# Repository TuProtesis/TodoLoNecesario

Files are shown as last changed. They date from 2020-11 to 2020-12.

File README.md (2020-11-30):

# TodoLoNecesario
Este repositorio contiene todos los archivos necesarios para guiarte en el proceso de ensamblado de tu prótesis.
Primero, compre todos los materiales de la lista de compra.
Luego, descarge todos los documentos del repositorio.
Por último, siga paso a paso las instrucciones del archivo "Manual para ensamblado de la prótesis".

Nota: Debe descargar el pdf "Lista de materiales de la protesis" para poder acceder a los enlaces de compra proporcionados.

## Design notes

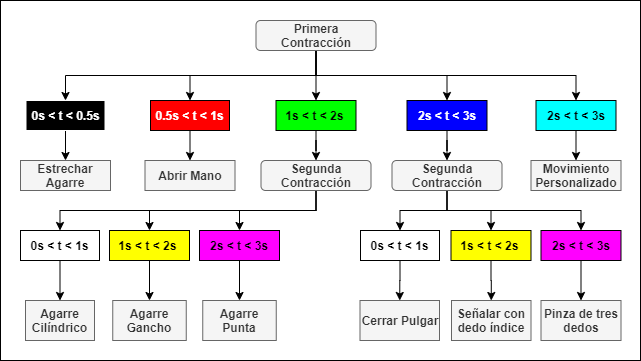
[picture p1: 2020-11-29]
Secuencias de Uso.png

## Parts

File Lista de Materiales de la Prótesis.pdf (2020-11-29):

# Lista de Materiales de la Prótesis

Materiales | Imagen del elemento | Precio unidad (USD) | Precio total (USD) | Lugar para comprar | Disponibilidad en Rep. Dom.
1x HATCHBOX PLA 3D Printer Filament, 1 kg Spool, 1.75 mm | | $19.99 | $19.99 | Amazon (https://www.amazon.com/-/es/filamento-impresora-3D-precisi%C3%B3n-dimensional/dp/B015I1CYFE?__mk_es_US=%C3%85M%C3%85%C5%BD%C3%95%C3%91) | En pocos lugares, recomendable comprar en el enlace proporcionado por nosotros.
1x Seamuing 6Pcs MG90S Micro Servo 9G | | $20.99 | $20.99 | Amazon (https://www.amazon.com/-/es/engranado-Helic%C3%B3ptero-Compatible-Raspberry-Proyecto/dp/B08BJPNTX9?__mk_es_US=%C3%85M%C3%85%C5%BD%C3%95%C3%91) | En pocos lugares, recomendable comprar en el enlace proporcionado por nosotros.
1x Minicargador portátil de 10000 mAh | | $16.99 | $16.99 | Amazon (https://www.amazon.com/-/es/Cargador-tel%C3%A9fono-port%C3%A1til-Powerpack-Compatible/dp/B07VGHLRTQ?__mk_es_US=%C3%85M%C3%85%C5%BD%C3%95%C3%91) | En pocos lugares, recomendable comprar en el enlace proporcionado por nosotros.
1x Hosyond Nano V3.0 ATmega328P | | $4.33 | $4.33 | Amazon (https://www.amazon.com/-/es/gp/product/B08915GQ89/ref=ppx_yo_dt_b_asin_title_o01_s00?ie=UTF8&psc=1) | En pocos lugares, recomendable comprar en el enlace proporcionado por nosotros.
1x Interruptor Pulsador | | $0.3 | $0.3 | Cabletronica | Puede comprarse en tiendas de internet si se desea. Enlace de Amazon. (https://www.amazon.com/dp/B00R17XUFC/ref=cm_sw_r_wa_apa_fabt1_ZG.WFb8VY8CMB)
1x Correa Velcro | | $3.07 | $6.15 | Ferretería Cuesta | Preferiblemente comprar en tiendas en el país.
1x Ácido muriático (Ácido Clorhídrico) | | $2.56 | $2.56 | Almacenes unidos | Preferiblemente comprar en tiendas en el país.
1x Agua oxigenada 30% | | $0.68 | $0.68 | Almacenes unidos | Preferiblemente comprar en tiendas en el país.

1x Acetona | $0.51 | $0.51 | Farmacia Farma Value | Preferiblemente comprar en tiendas en el país .
1x Baquelita ónica electr | $1 | $1 | Cabletronica | Puede comprarse en tiendas de internet si se desea . Enlace de Amazon . (https://www.amazon.com/-/es/laminado-unidades-laminada-bricolaje-circuito/dp/B01MCVLDDZ)
Resistencias 2 de 100 ohms 2 de 1k ohms 1 de 2k ohms 1 de 220 ohm s Total: 6 | $0.017 | $0.10 | Cabletrónica | Puede comprarse en tiendas de internet si se desea . Enlace de Amazon . (https://www.amazon.com/-/es/valores-resistencias-resistencia-proyectos-experimentos/dp/B07BKRS4QZ)
1x Led RGB | $0.09 | $0.09 | Cabletronica | Puede comprarse en tiendas de internet si se desea . Enlace de Amazon . (https://www.amazon.com/-/es/Tri-Color-Multicolor-Resistencias-Incluido-emisores/dp/B077XGF3YR?__mk_es_US=%C3%85M%C3%85%C5%BD%C3%95%C3%91)
1x Pin header hembra | $1.79 | $1.79 | Cabletronica | Puede comprarse en tiendas de internet si se desea . Enlace de Amazon . (https://www.amazon.com/-/es/honbay-40-pines-hembra-conector-Arduino/dp/B06Y4S6G29?__mk_es_US=%C3%85M%C3%85%C5%BD%C3%95%C3%91&s=electronics)
Conector de crimpado (19 c/u. ) Total: 38 | $0.034 | $1.3 | Cabletr ónica | Puede comprarse en tiendas de internet si se desea .
1x Estaño para soldar | $3 | $3 | Cabletronica | Puede comprarse en tiendas de internet si se desea . Enlace de Amazon . (https://www.amazon.com/-/es/AUSTOR-60-40-soldadura-3-53-0-039/dp/B073LT2PKB?__mk_es_US=%C3%85M%C3%85%C5%BD%C3%95%C3%91)
1x Módulo Bluetooth 4.0 para Arduino iOS Android CC2540 CC2541 (2 unidades) | $4 | $4 | Amazon (https://www.amazon.com/-/es/gp/product/B01G9KSAF6/ref=ppx_yo_dt_b_asin_title_o07_s00?ie=UTF8&psc=1) | En pocos lugares, recomendable comprar en el enlace proporcionado por nosotros.

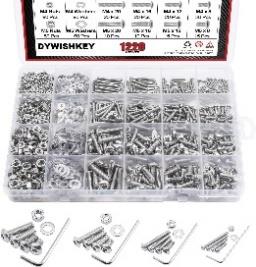
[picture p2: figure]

1x DYWISHKEY 1220 piezas M2 M3 M4 M5, 304 acero inoxidable hexagonal botón cabeza tornillos tuercas arandelas surtido Kit con llaves hexagonales | $26.98 | $26.98 | Amazon (https://www.amazon.com/-/es/DYWISHKEY-inoxidable-hexagonal-tornillos-hexagonales/dp/B07QLRKYR7?__mk_es_US=%C3%85M%C3%85%C5%BD%C3%95%C3%91) | Recomendable comprar los tornillos por separado en ferreterías del país . Pueden tener el tipo de cabeza que usted prefiera.

$
126.8

6 (USD)

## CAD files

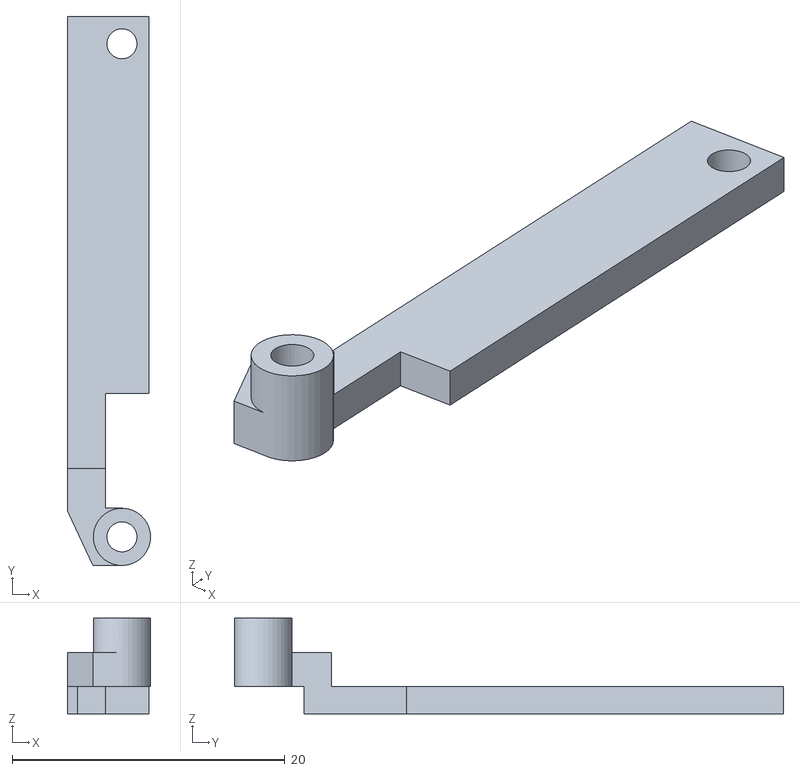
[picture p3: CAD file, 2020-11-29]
Impresión/Anular/Anular_Pieza5.STL
6.10 x 40.2 x 7.00

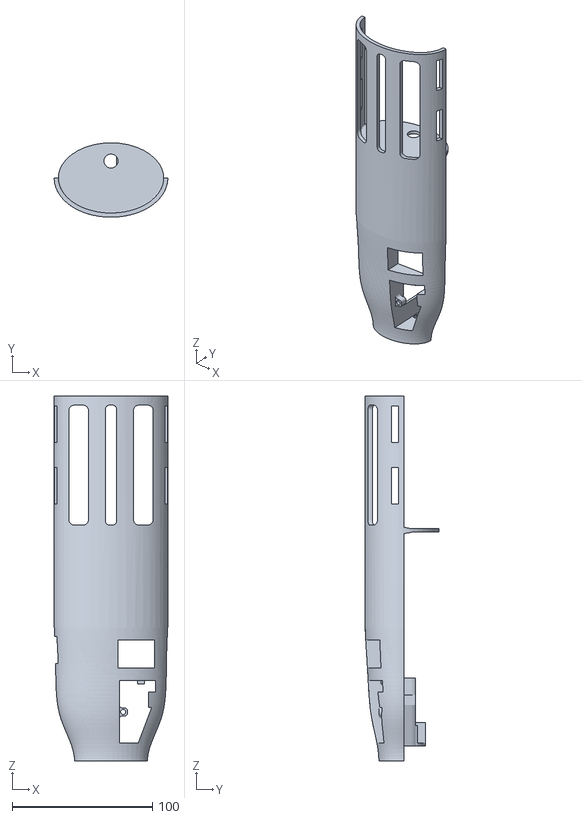
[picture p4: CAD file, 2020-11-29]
Impresión/Brazo/Brazo_Pieza15.STL
81.0 x 53.0 x 259.9

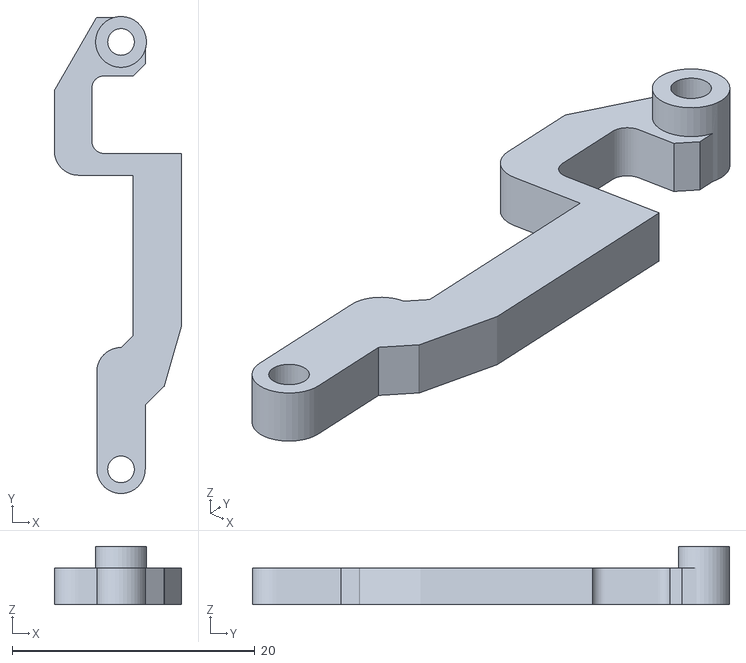
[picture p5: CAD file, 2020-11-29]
Impresión/Mayor/Mayor_Pieza6.STL
10.5 x 39.3 x 4.80

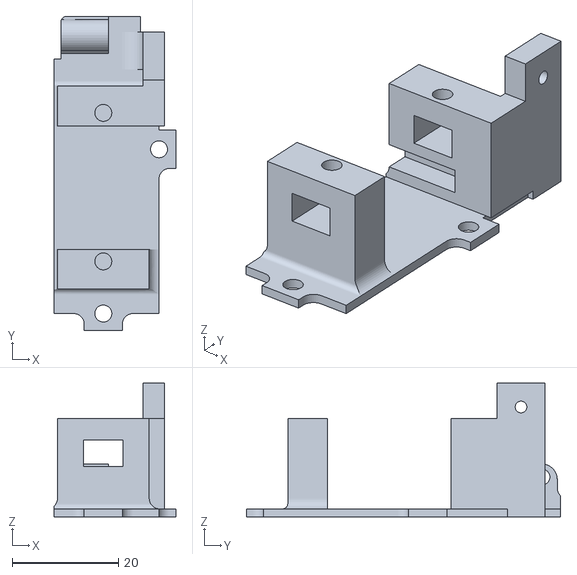
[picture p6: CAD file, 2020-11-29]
Impresión/Meñique/Meñique_Pieza1.STL
23.0 x 59.2 x 25.2

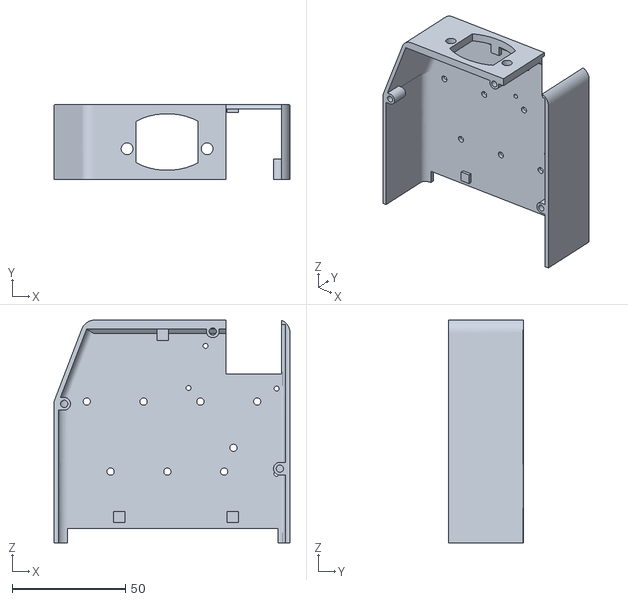
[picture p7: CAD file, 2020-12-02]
Impresión/Palma/Palma_Pieza12_para mano derecha.STL
104.3 x 33.0 x 98.5

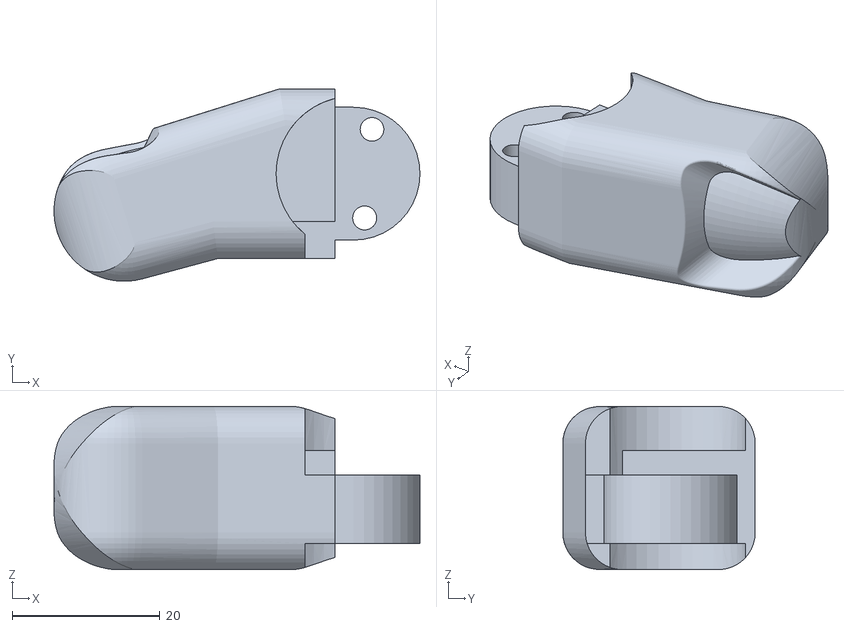
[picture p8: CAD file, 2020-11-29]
Impresión/Pulgar/Pulgar_Pieza7.STL
49.6 x 26.1 x 22.1

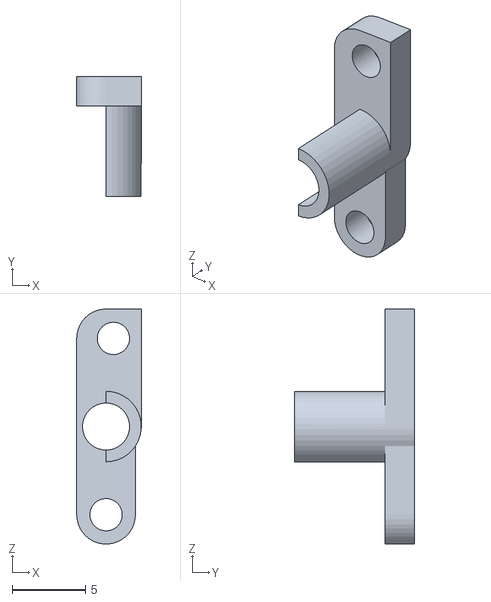
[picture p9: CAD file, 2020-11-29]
Impresión/Índice/Índice_Pieza4.STL
4.40 x 8.15 x 16.0

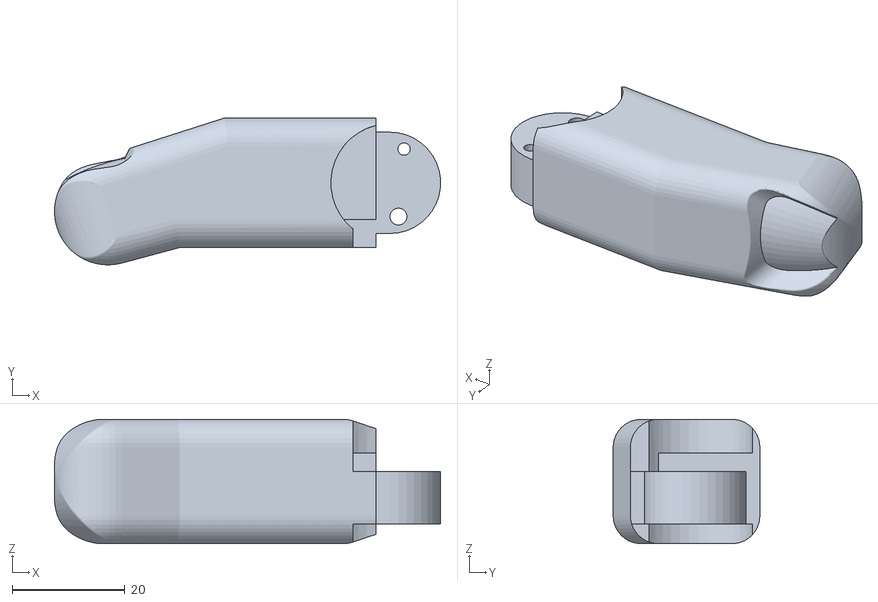
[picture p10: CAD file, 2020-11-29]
Impresión/Anular/Anular_Pieza7.STL
68.6 x 26.1 x 22.1

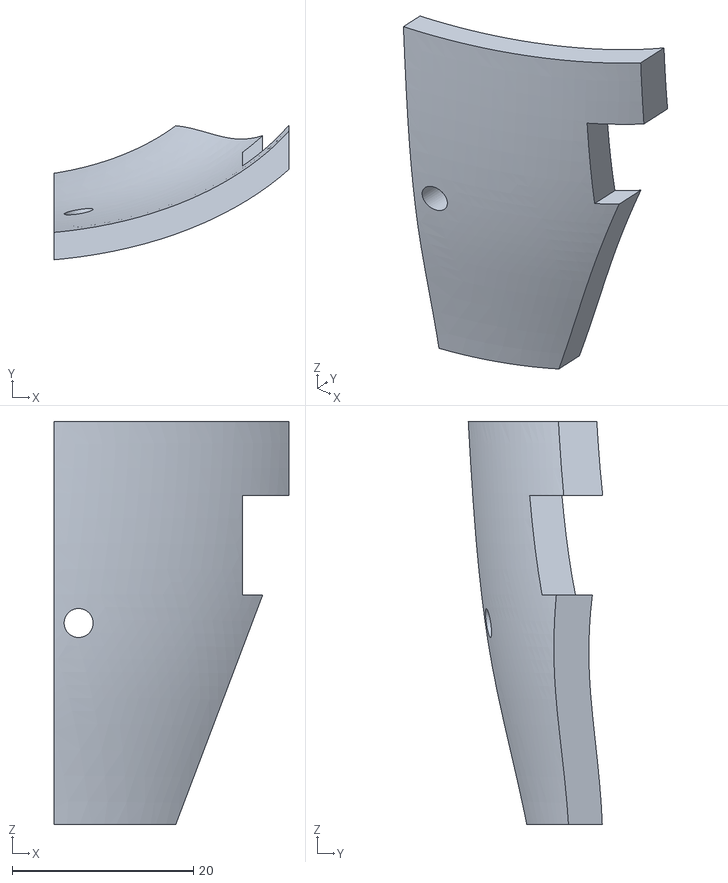
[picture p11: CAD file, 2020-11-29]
Impresión/Brazo/Brazo_Pieza17.STL
25.9 x 14.8 x 44.4

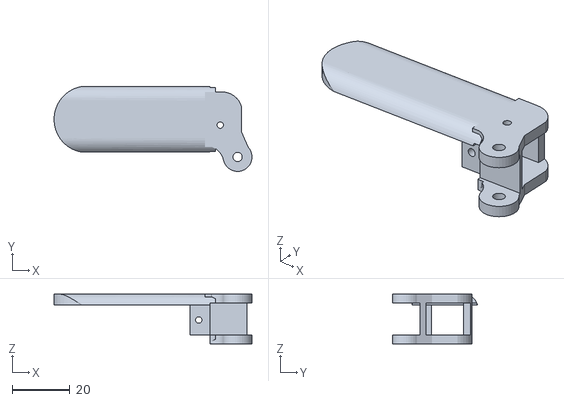
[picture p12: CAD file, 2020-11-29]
Impresión/Mayor/Mayor_Pieza9.STL
68.4 x 29.3 x 17.2

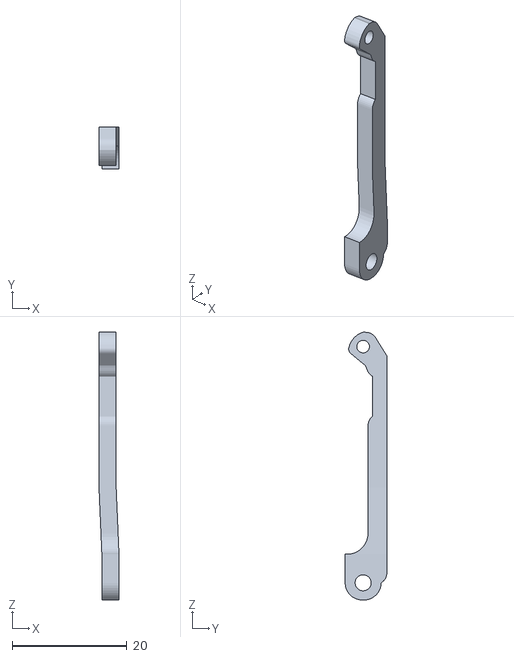
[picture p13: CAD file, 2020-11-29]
Impresión/Meñique/Meñique_Pieza3.STL
3.50 x 7.30 x 46.8

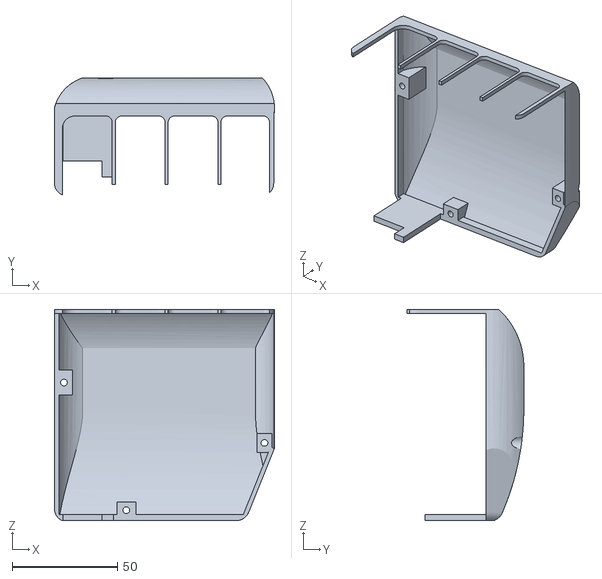
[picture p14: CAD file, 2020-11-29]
Impresión/Palma/Palma_Pieza14.STL
104.6 x 55.5 x 100.5

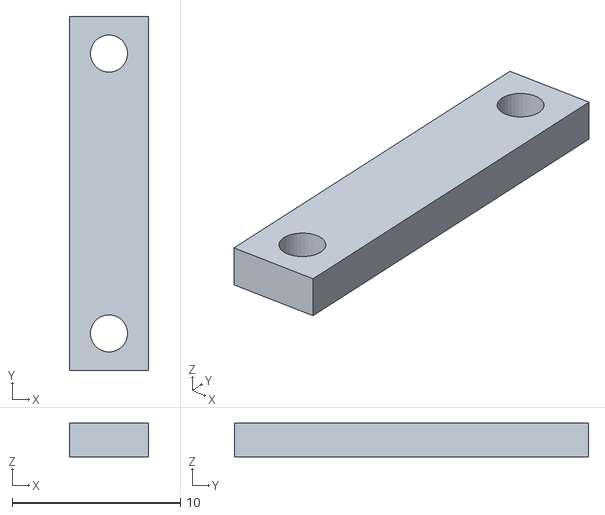
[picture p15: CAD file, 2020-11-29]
Impresión/Pulgar/Pulgar_Pieza10.STL
4.70 x 21.0 x 2.00

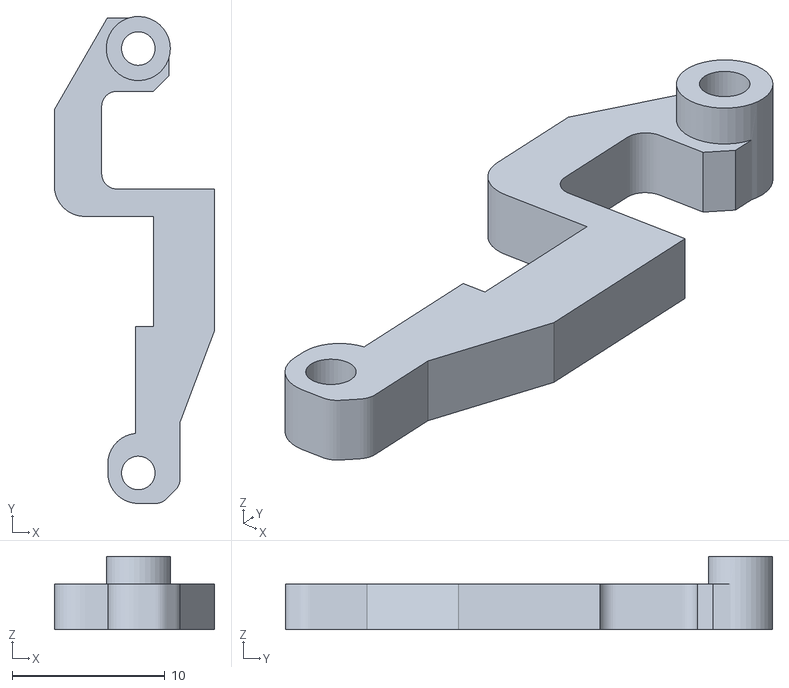
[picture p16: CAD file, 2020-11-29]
Impresión/Índice/Índice_Pieza6.STL
10.5 x 31.9 x 4.80

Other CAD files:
Impresión/Brazo/Brazo_Pieza16.STL
Impresión/Meñique/Meñique_Pieza8.STL
Impresión/Anular/Anular_Pieza2.STL
Impresión/Anular/Anular_Pieza4.STL
Impresión/Anular/Anular_Pieza6.STL
Impresión/Anular/Anular_Pieza8.STL
Impresión/Anular/Anular_Pieza9.STL
Impresión/Mayor/Mayor_Pieza2.STL
Impresión/Mayor/Mayor_Pieza4.STL
Impresión/Mayor/Mayor_Pieza5.STL
Impresión/Mayor/Mayor_Pieza8.STL
Impresión/Mayor/Mayor_pieza7.STL
Impresión/Meñique/Meñique_Pieza2.STL
Impresión/Meñique/Meñique_Pieza4.STL
Impresión/Meñique/Meñique_Pieza5.STL
Impresión/Meñique/Meñique_Pieza6.STL
Impresión/Meñique/Meñique_Pieza7.STL
Impresión/Meñique/Meñique_Pieza9.STL
Impresión/Palma/Palma_Pieza12_Para mano izquierda.STL
Impresión/Palma/Palma_Pieza13.STL
Impresión/Pulgar/Pulgar_Pieza11.STL
Impresión/Pulgar/Pulgar_Pieza8.STL
Impresión/Pulgar/Pulgar_Pieza9.STL
Impresión/Índice/Índice_Pieza1.STL
Impresión/Índice/Índice_Pieza2.STL
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

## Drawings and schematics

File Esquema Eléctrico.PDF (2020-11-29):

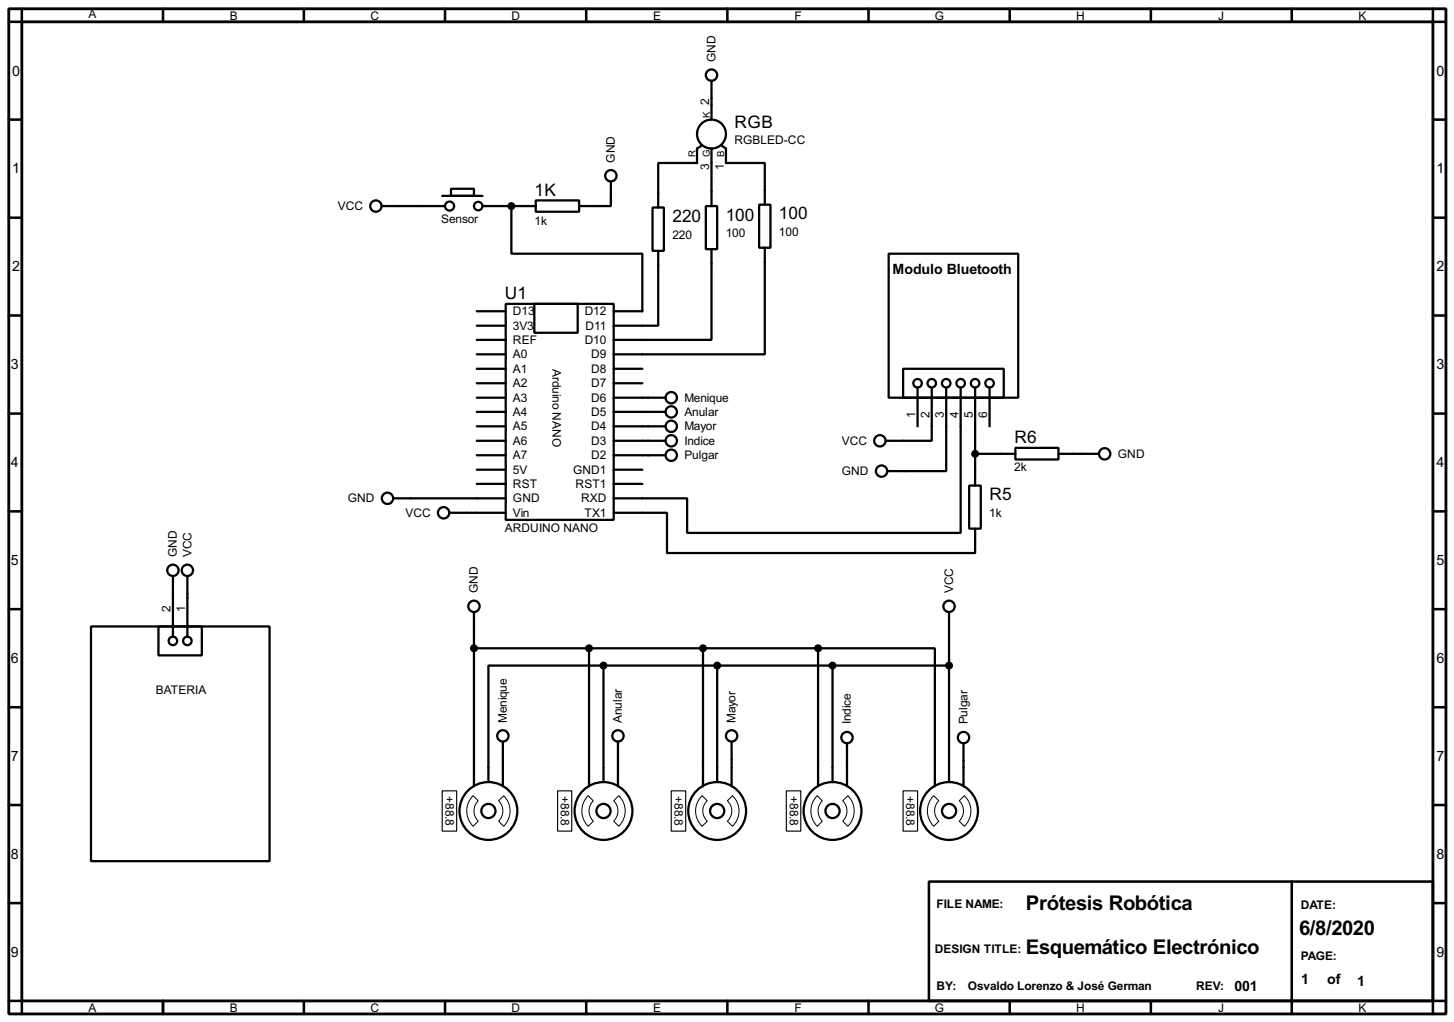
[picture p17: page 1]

Indice Mayor Anular Menique

DESIGN TITLE: Esquemático Electrónico

Osvaldo Lorenzo & José German

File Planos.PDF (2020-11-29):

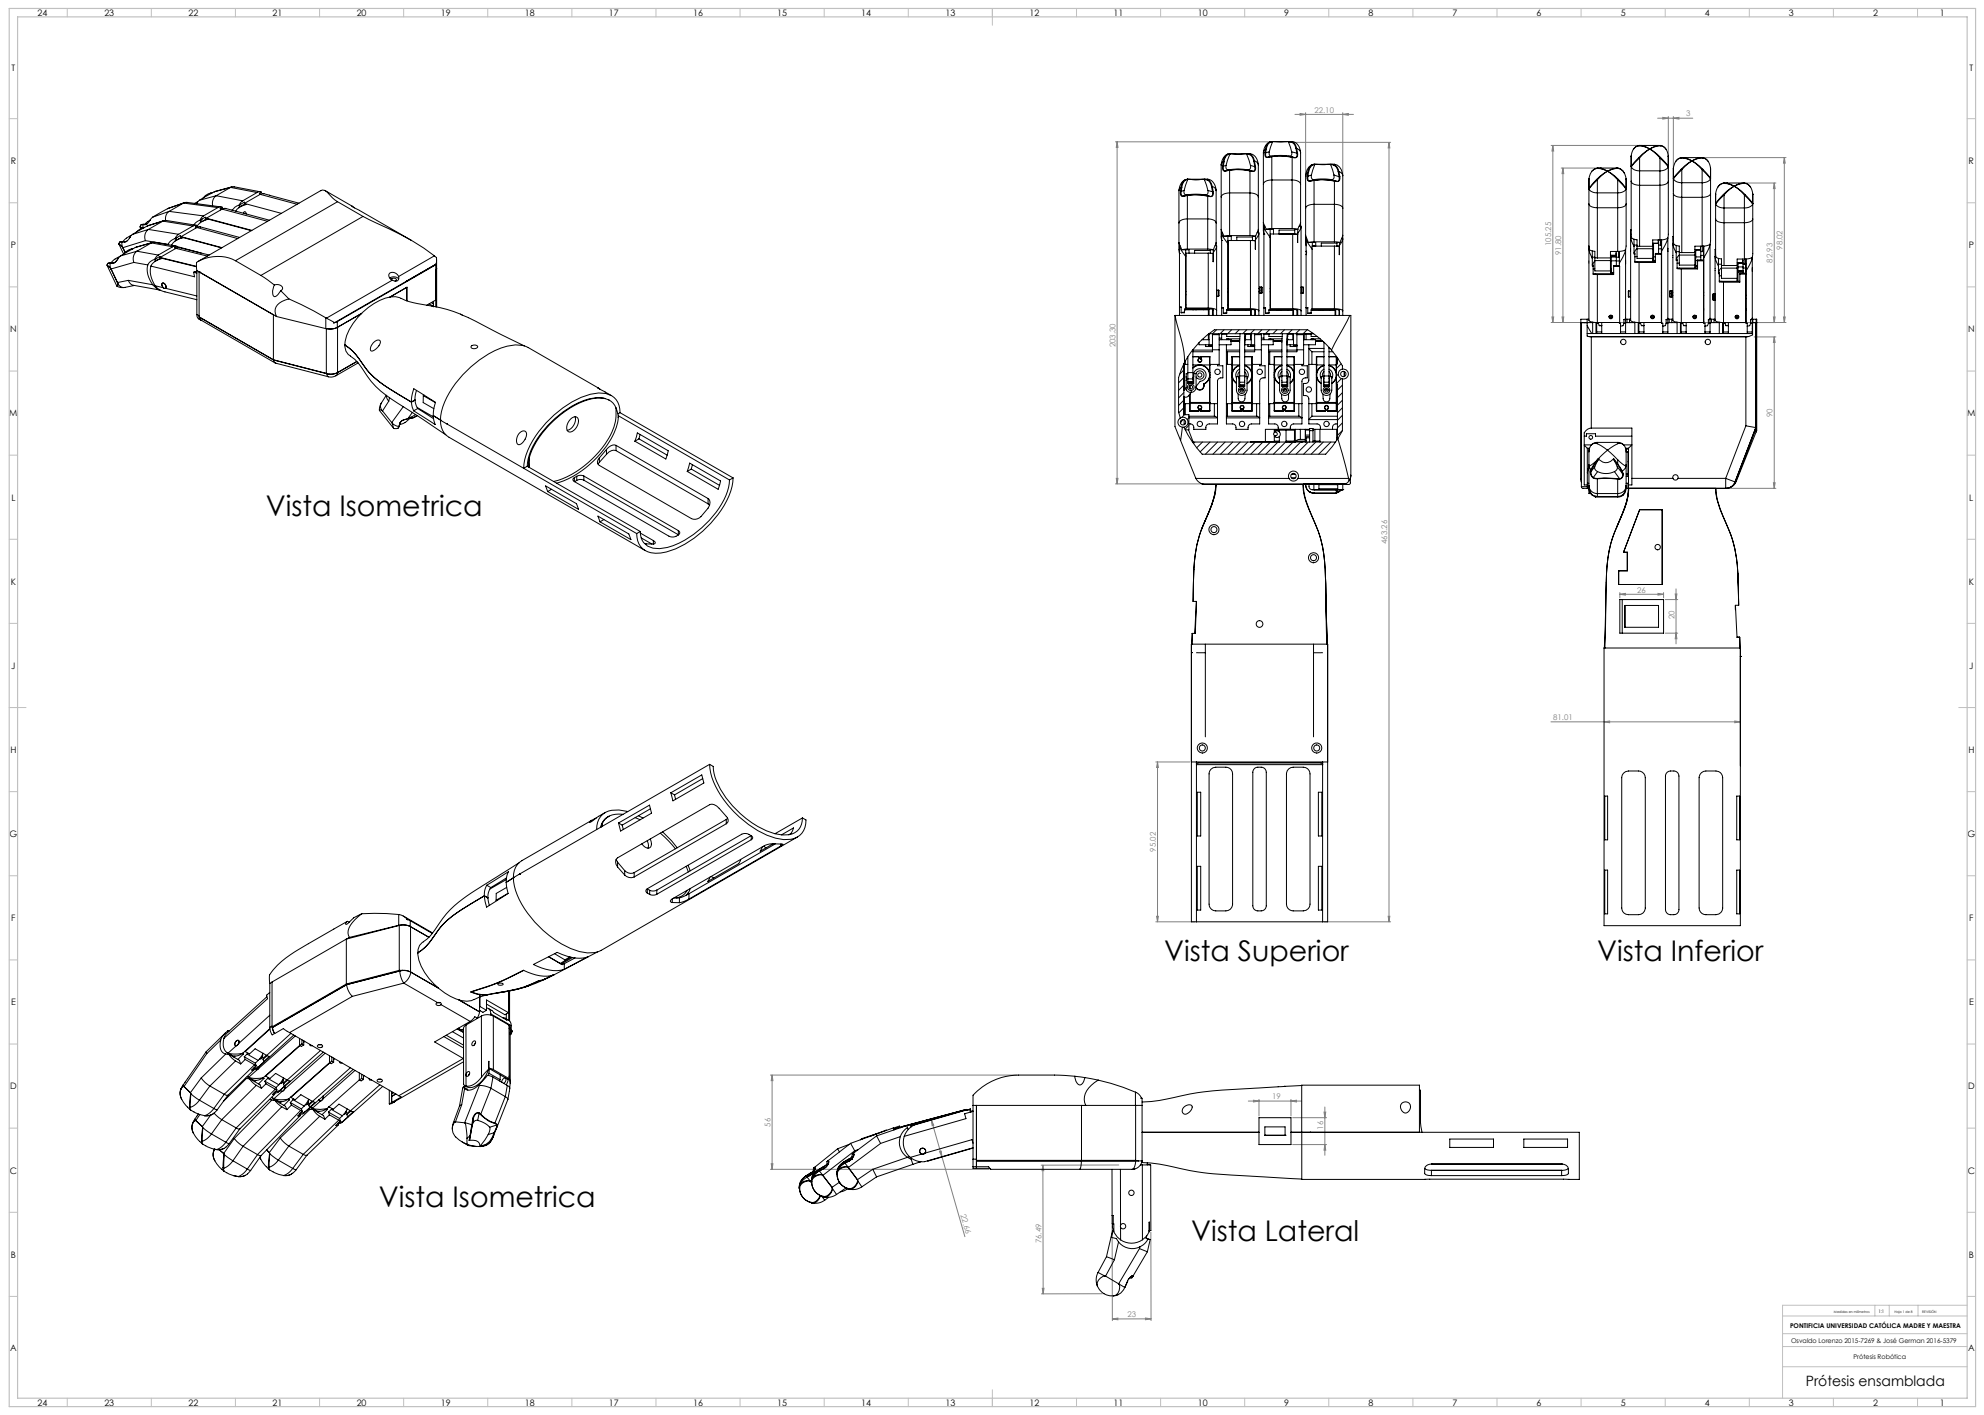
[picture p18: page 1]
Vista Lateral; Vista Isometrica; Vista Superior; Vista Inferior; Hoja 1 de 8; REVISIÓN; Prótesis Robótica; Medidas en milímetros

PONTIFICIA UNIVERSIDAD CATÓLICA MADRE Y MAESTRA
Osvaldo Lorenzo 2015-7269 & José German 2016-5379
Prótesis ensamblada

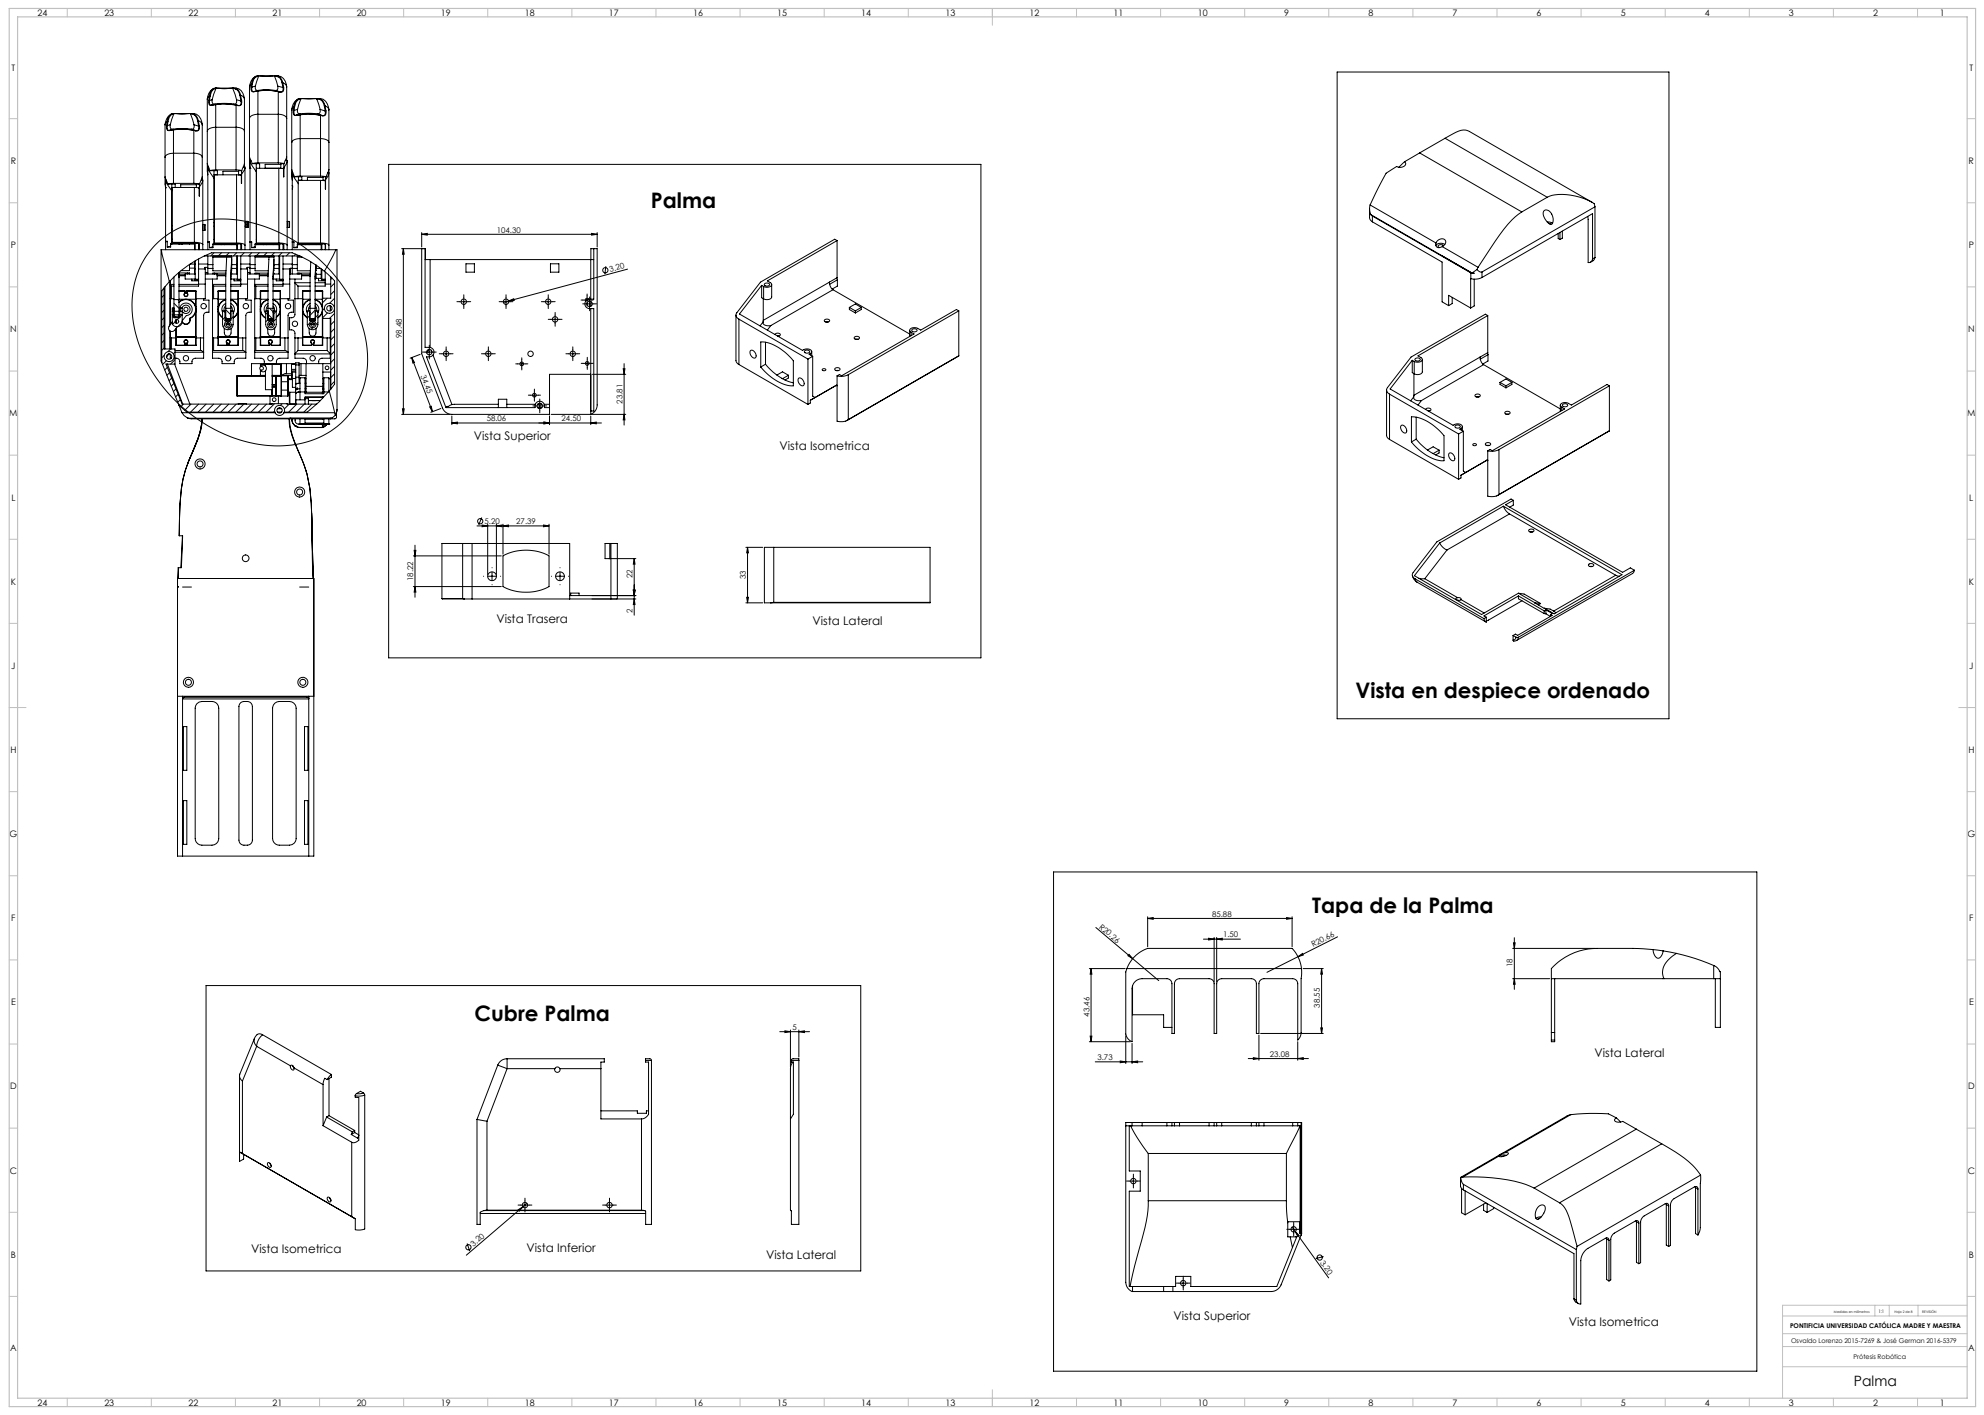
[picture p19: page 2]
Vista Superior; Vista Isometrica 33; Vista Lateral; Vista Trasera; Vista Isometrica; Vista Inferior; Tapa de la Palma; Cubre Palma; Hoja 2 de 8; REVISIÓN

Vista en despiece ordenado

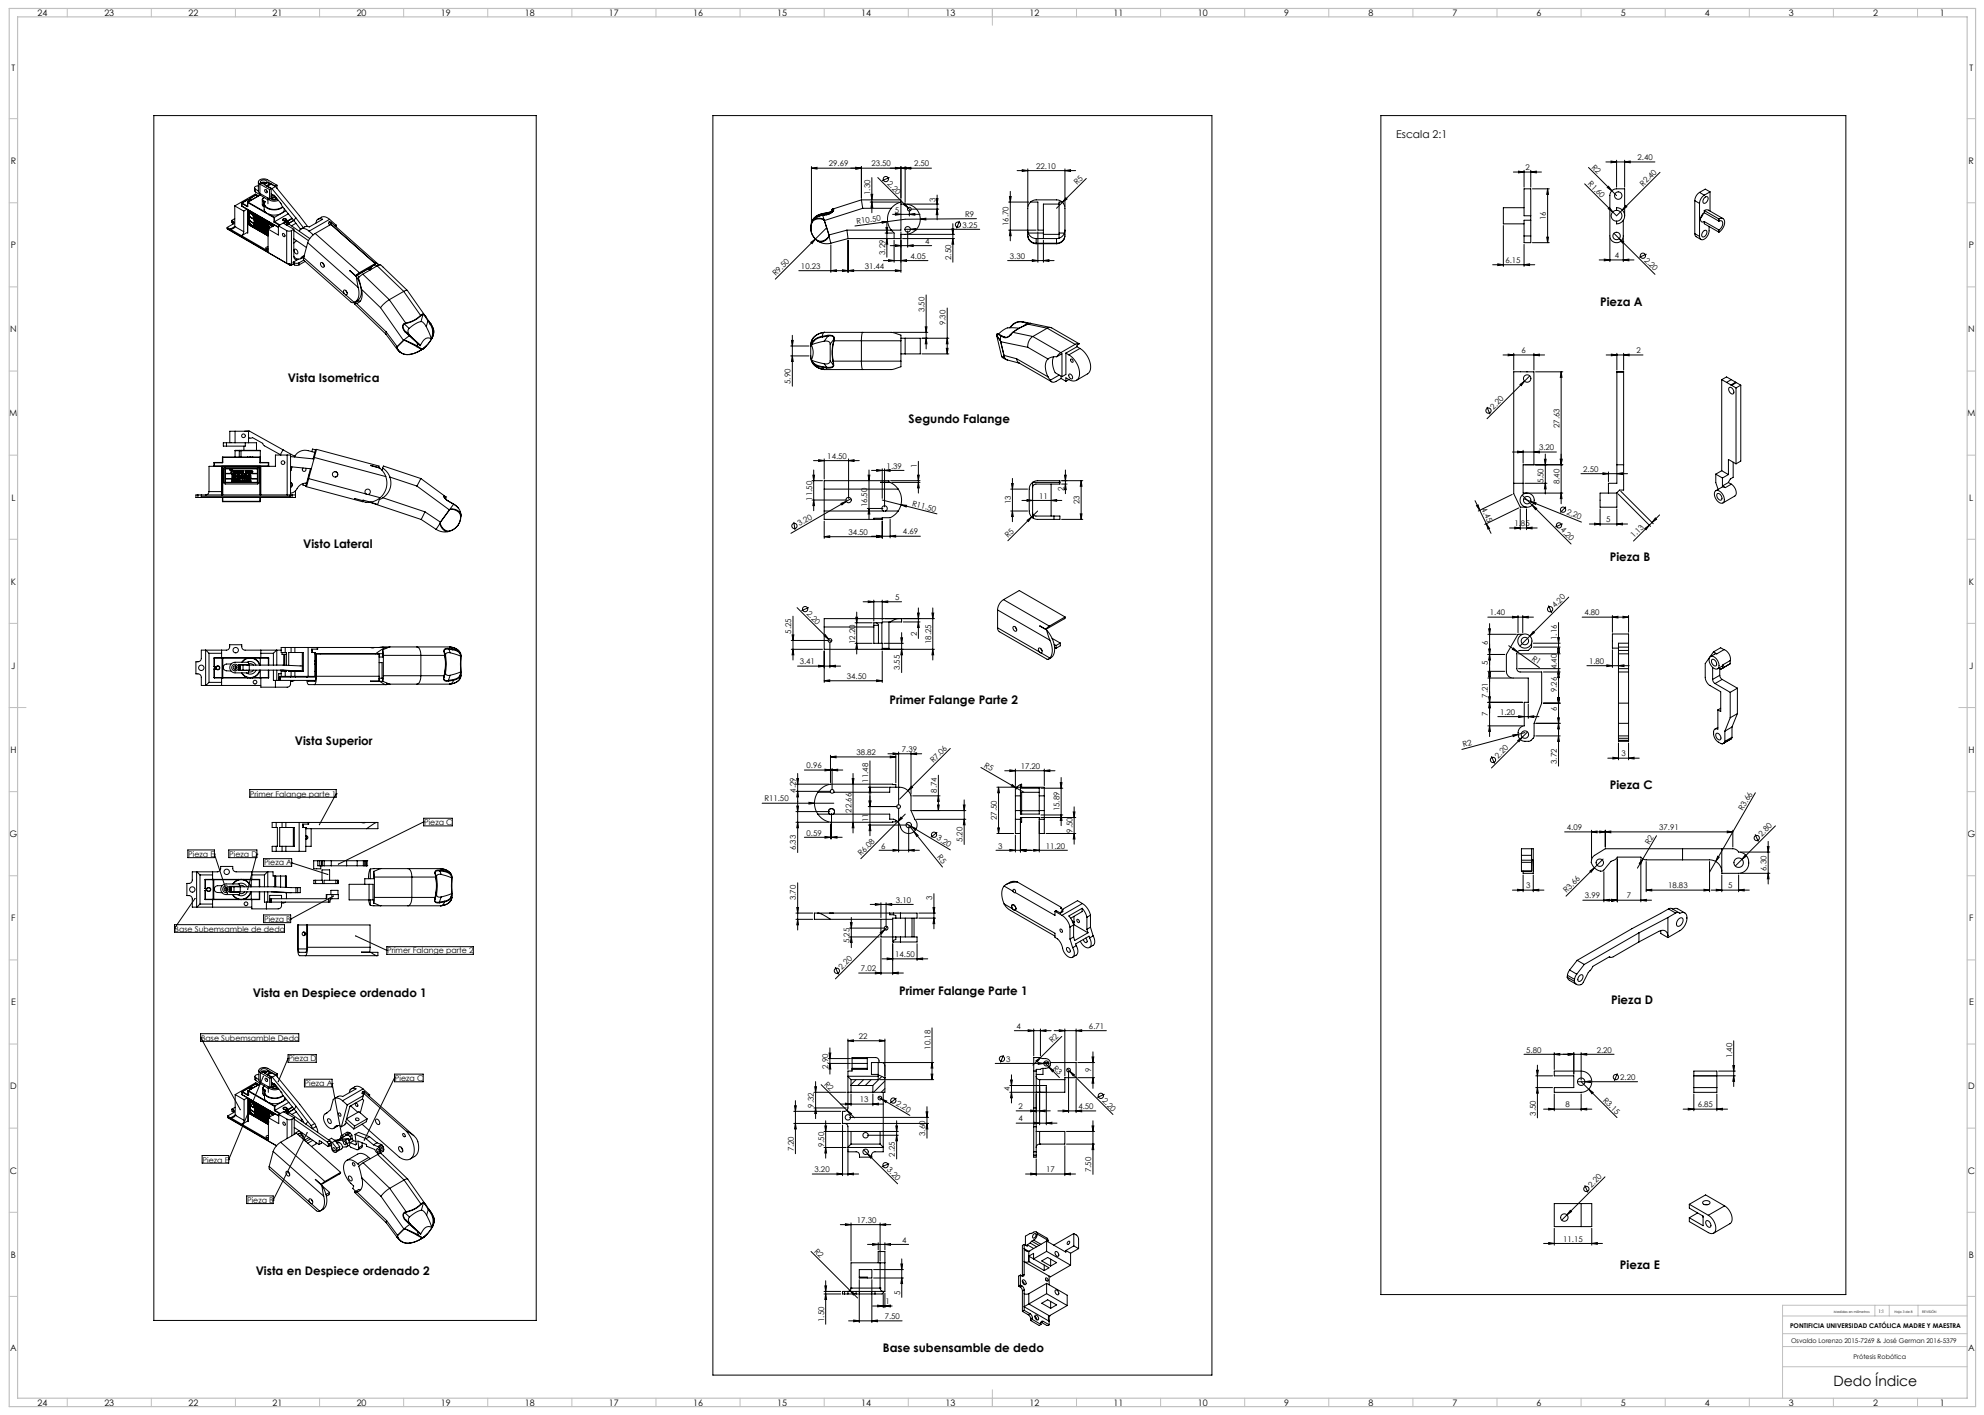
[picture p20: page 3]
Vista Isometrica; Visto Lateral; Vista Superior; Segundo Falange; Pieza D; Pieza C; Pieza A; Pieza B; Pieza E; Pieza C Pieza A; Escala 2:1; Hoja 3 de 8; REVISIÓN; Dedo Índice

Primer Falange Parte 2

Primer Falange parte 1

Base Subemsamble de dedo

Primer Falange parte 2

Primer Falange Parte 1

Vista en Despiece ordenado 1

Base Subemsamble Dedo

Vista en Despiece ordenado 2

Base subensamble de dedo

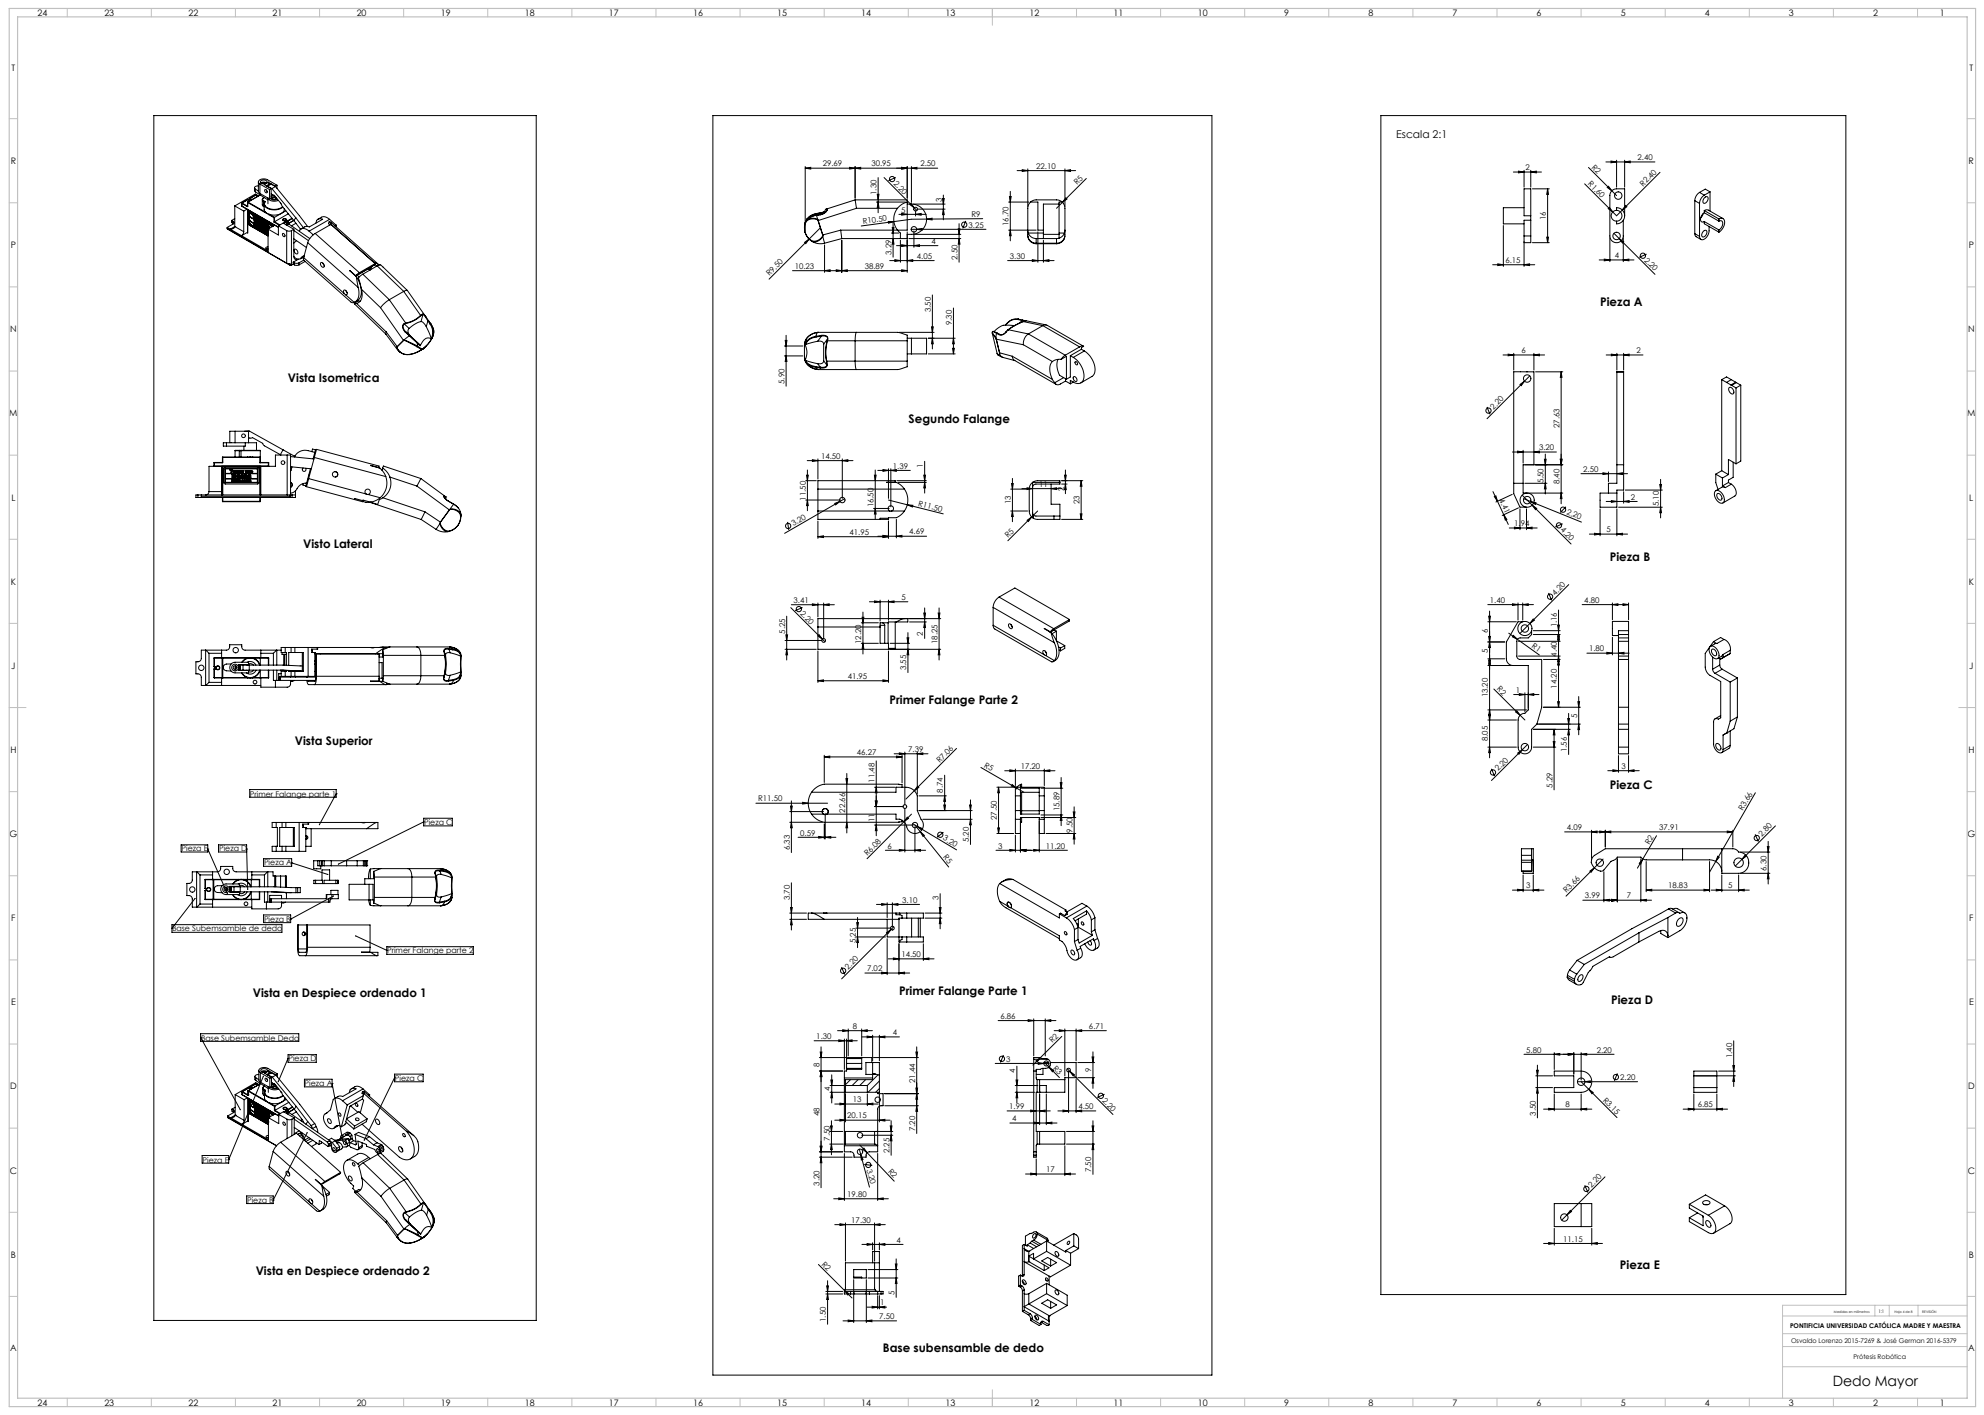
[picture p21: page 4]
Vista Isometrica; Visto Lateral; Vista Superior; Segundo Falange; Pieza D; Pieza C; Pieza A; Pieza B; Pieza E Pieza D; Pieza E; Pieza C Pieza A; Escala 2:1; Hoja 4 de 8; REVISIÓN; Dedo Mayor

Primer Falange Parte 2

Primer Falange parte 1

Base Subemsamble de dedo

Primer Falange parte 2

Primer Falange Parte 1

Vista en Despiece ordenado 1

Base Subemsamble Dedo

Vista en Despiece ordenado 2

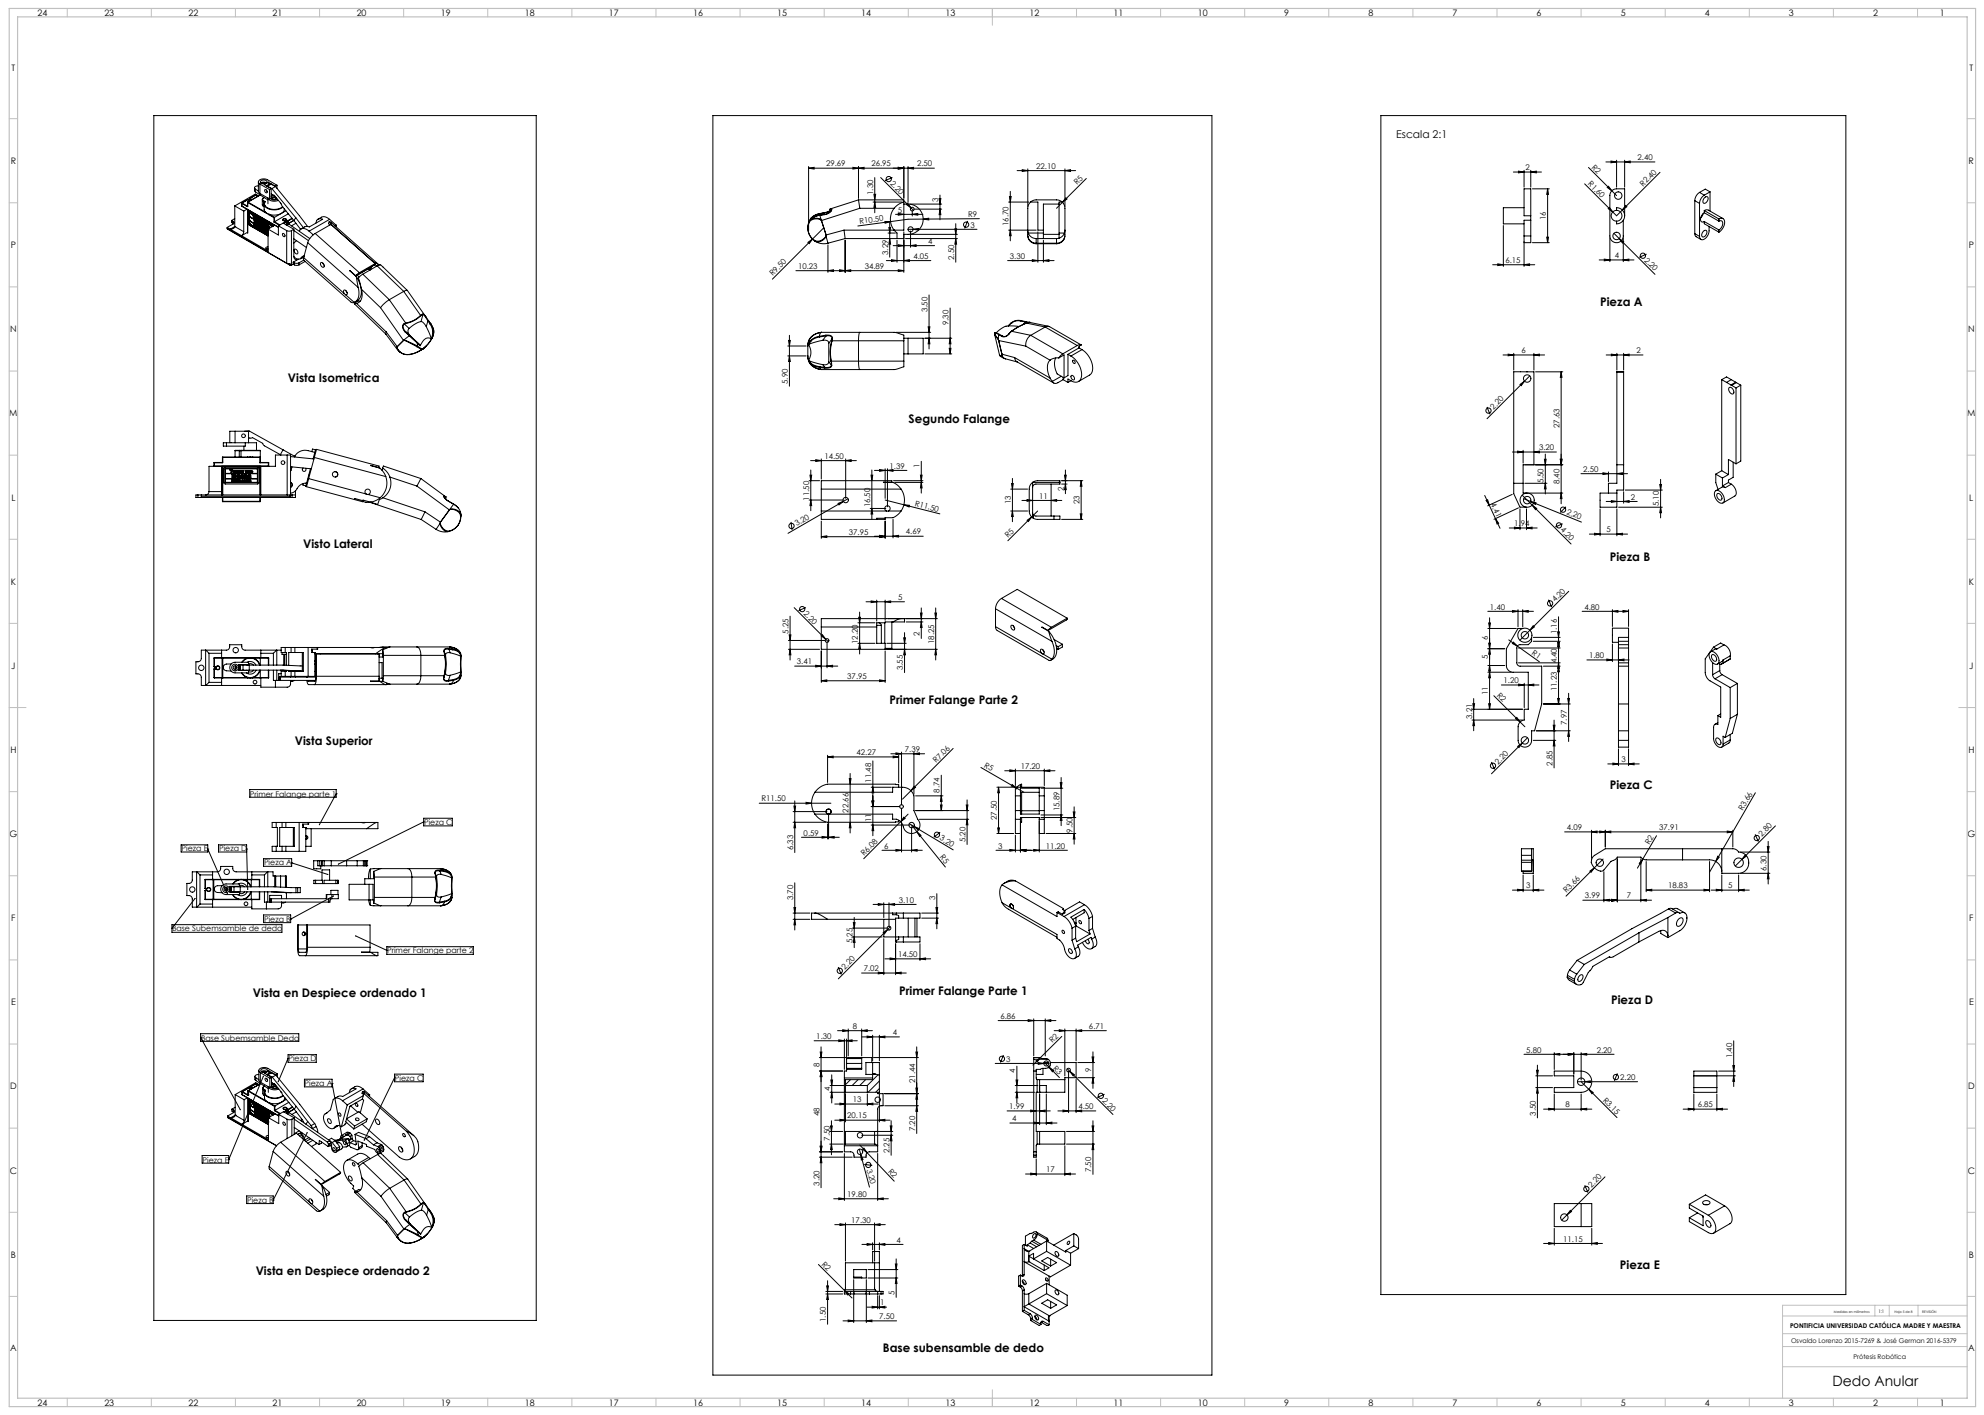
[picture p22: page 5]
Vista Isometrica; Visto Lateral; Vista Superior; Segundo Falange; Pieza D; Pieza C; Pieza A; Pieza B; Pieza E Pieza D; Pieza E; Pieza C Pieza A; Escala 2:1; Hoja 5 de 8; REVISIÓN; Dedo Anular

Primer Falange Parte 2

Primer Falange parte 1

Base Subemsamble de dedo

Primer Falange parte 2

Primer Falange Parte 1

Vista en Despiece ordenado 1

Base Subemsamble Dedo

Vista en Despiece ordenado 2

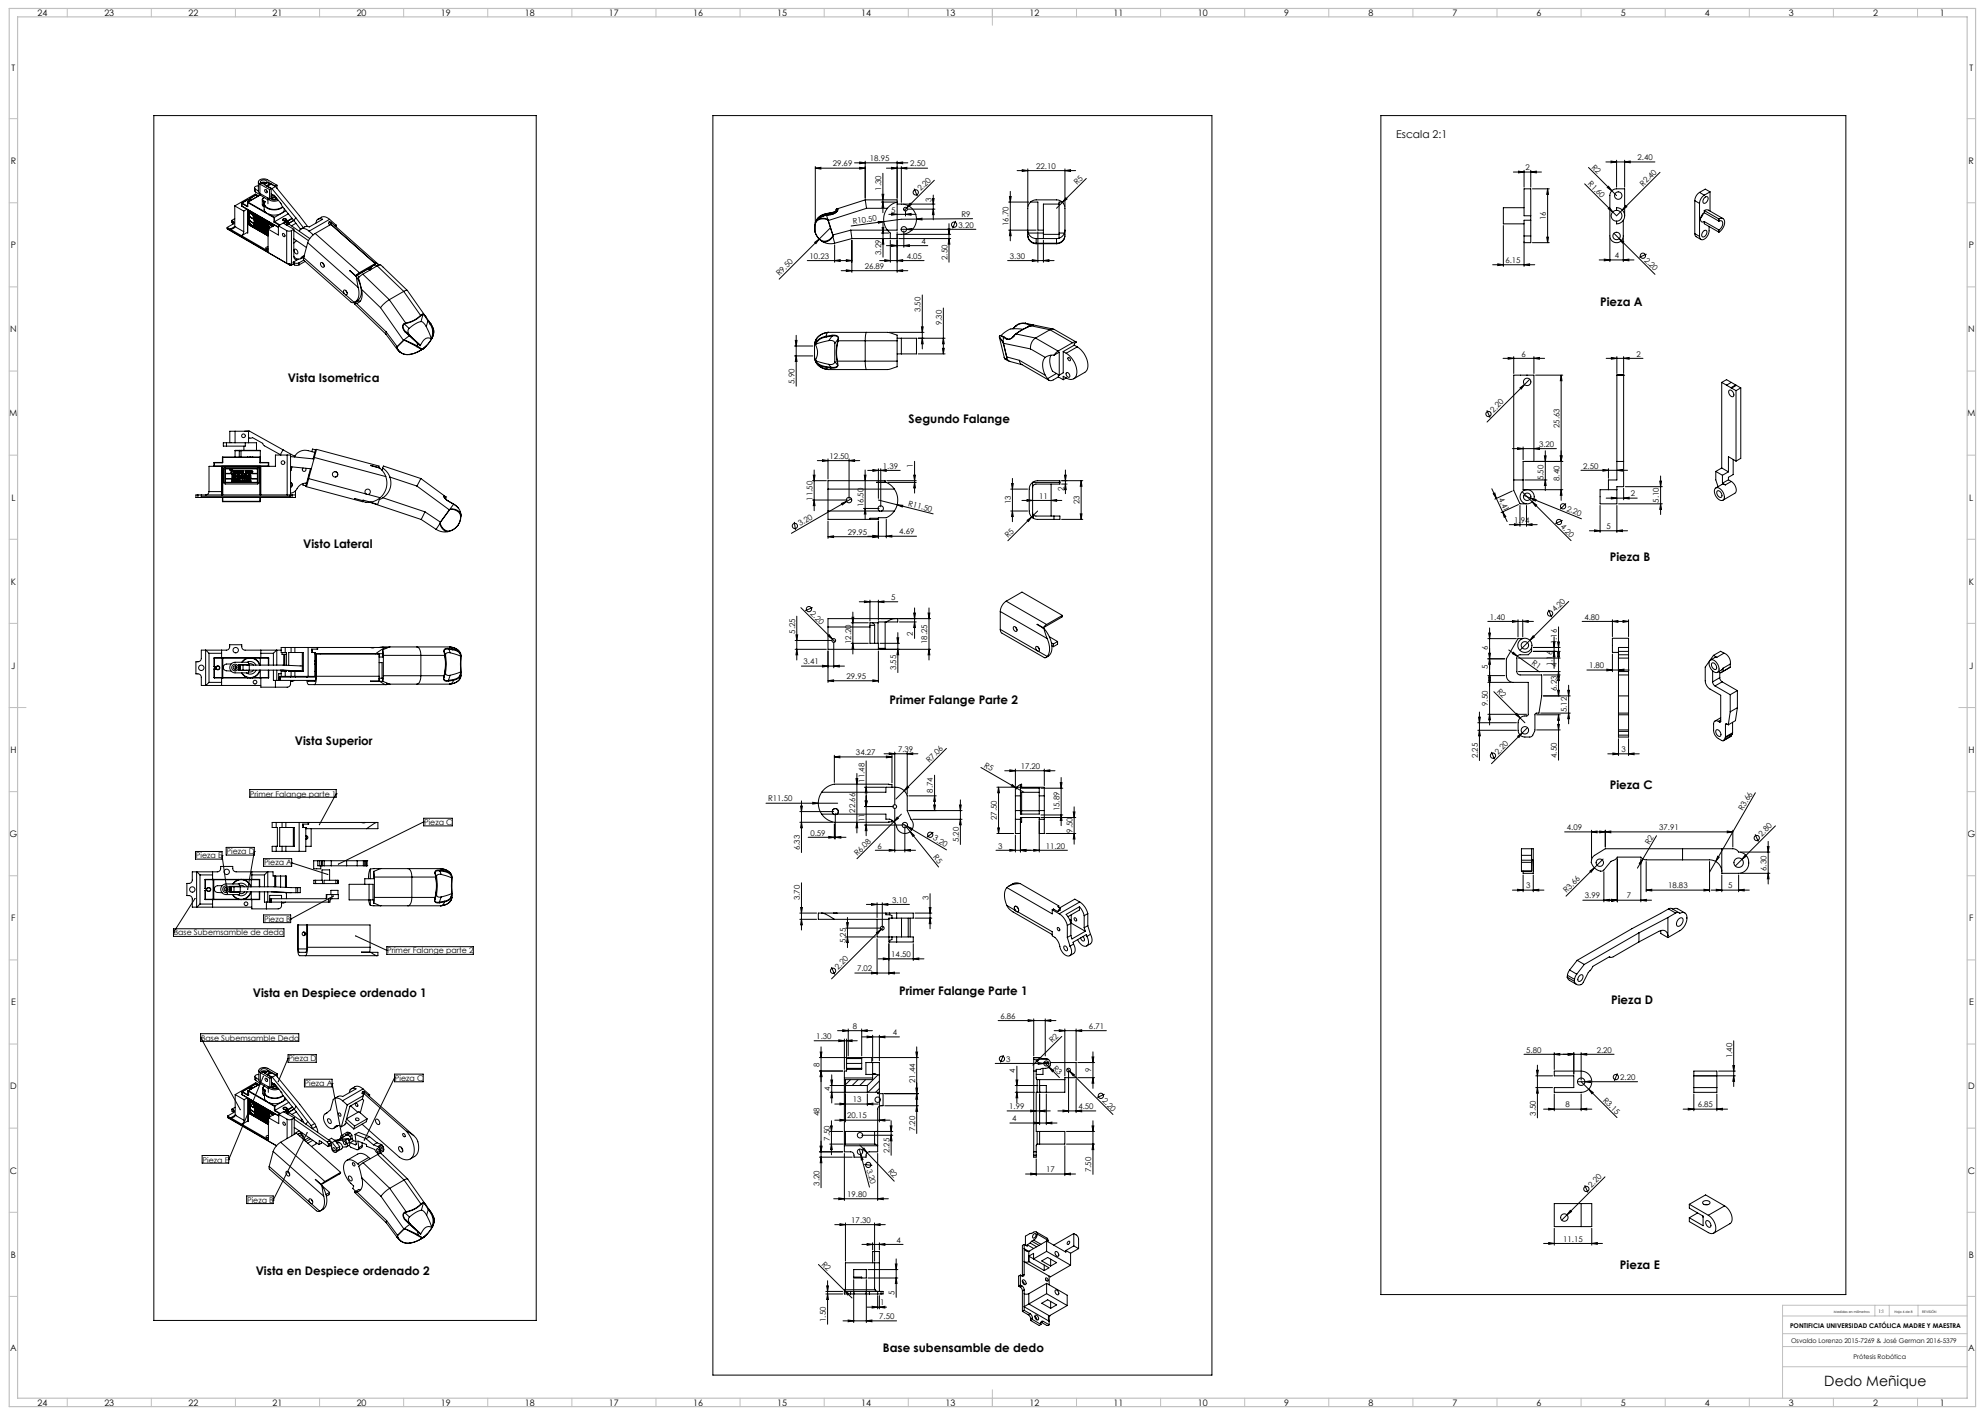
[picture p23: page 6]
Vista Isometrica; Visto Lateral; Vista Superior; Segundo Falange; Pieza D; Pieza C; Pieza A; Pieza B; Pieza E Pieza D; Pieza E; Pieza C Pieza A; Escala 2:1; Hoja 6 de 8; REVISIÓN; Dedo Meñique

Primer Falange Parte 2

Primer Falange parte 1

Base Subemsamble de dedo

Primer Falange parte 2

Primer Falange Parte 1

Vista en Despiece ordenado 1

Base Subemsamble Dedo

Vista en Despiece ordenado 2

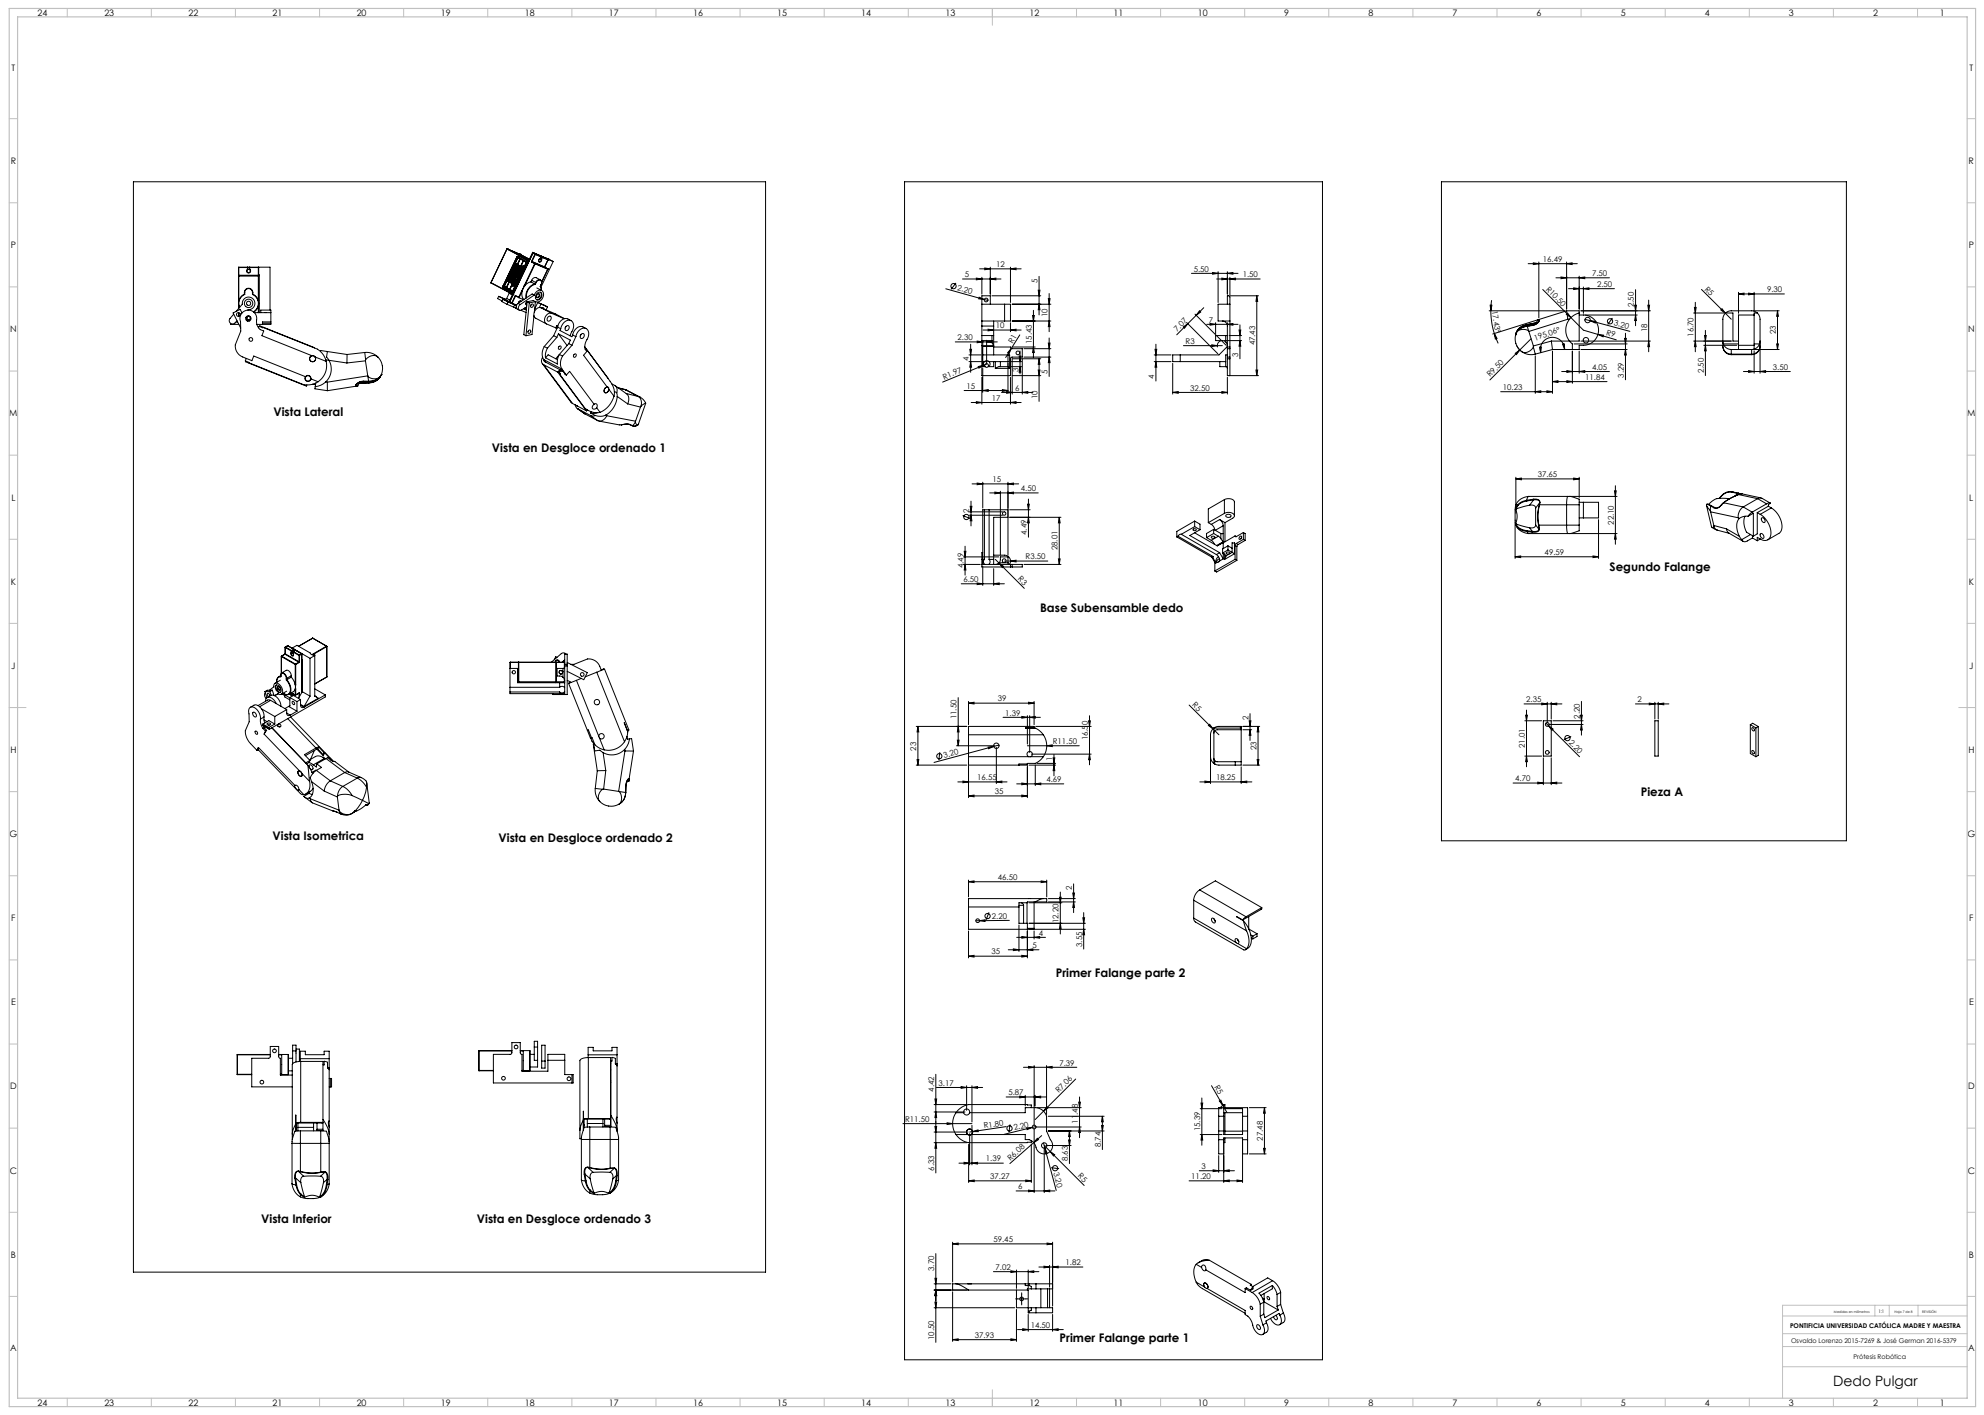
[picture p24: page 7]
Vista Lateral; Vista Isometrica; Vista Inferior; Primer Falange parte 2; Primer Falange parte 1; Segundo Falange; Pieza A; Hoja 7 de 8; REVISIÓN; Dedo Pulgar

Vista en Desgloce ordenado 1

Base Subensamble dedo

Vista en Desgloce ordenado 2

Vista en Desgloce ordenado 3

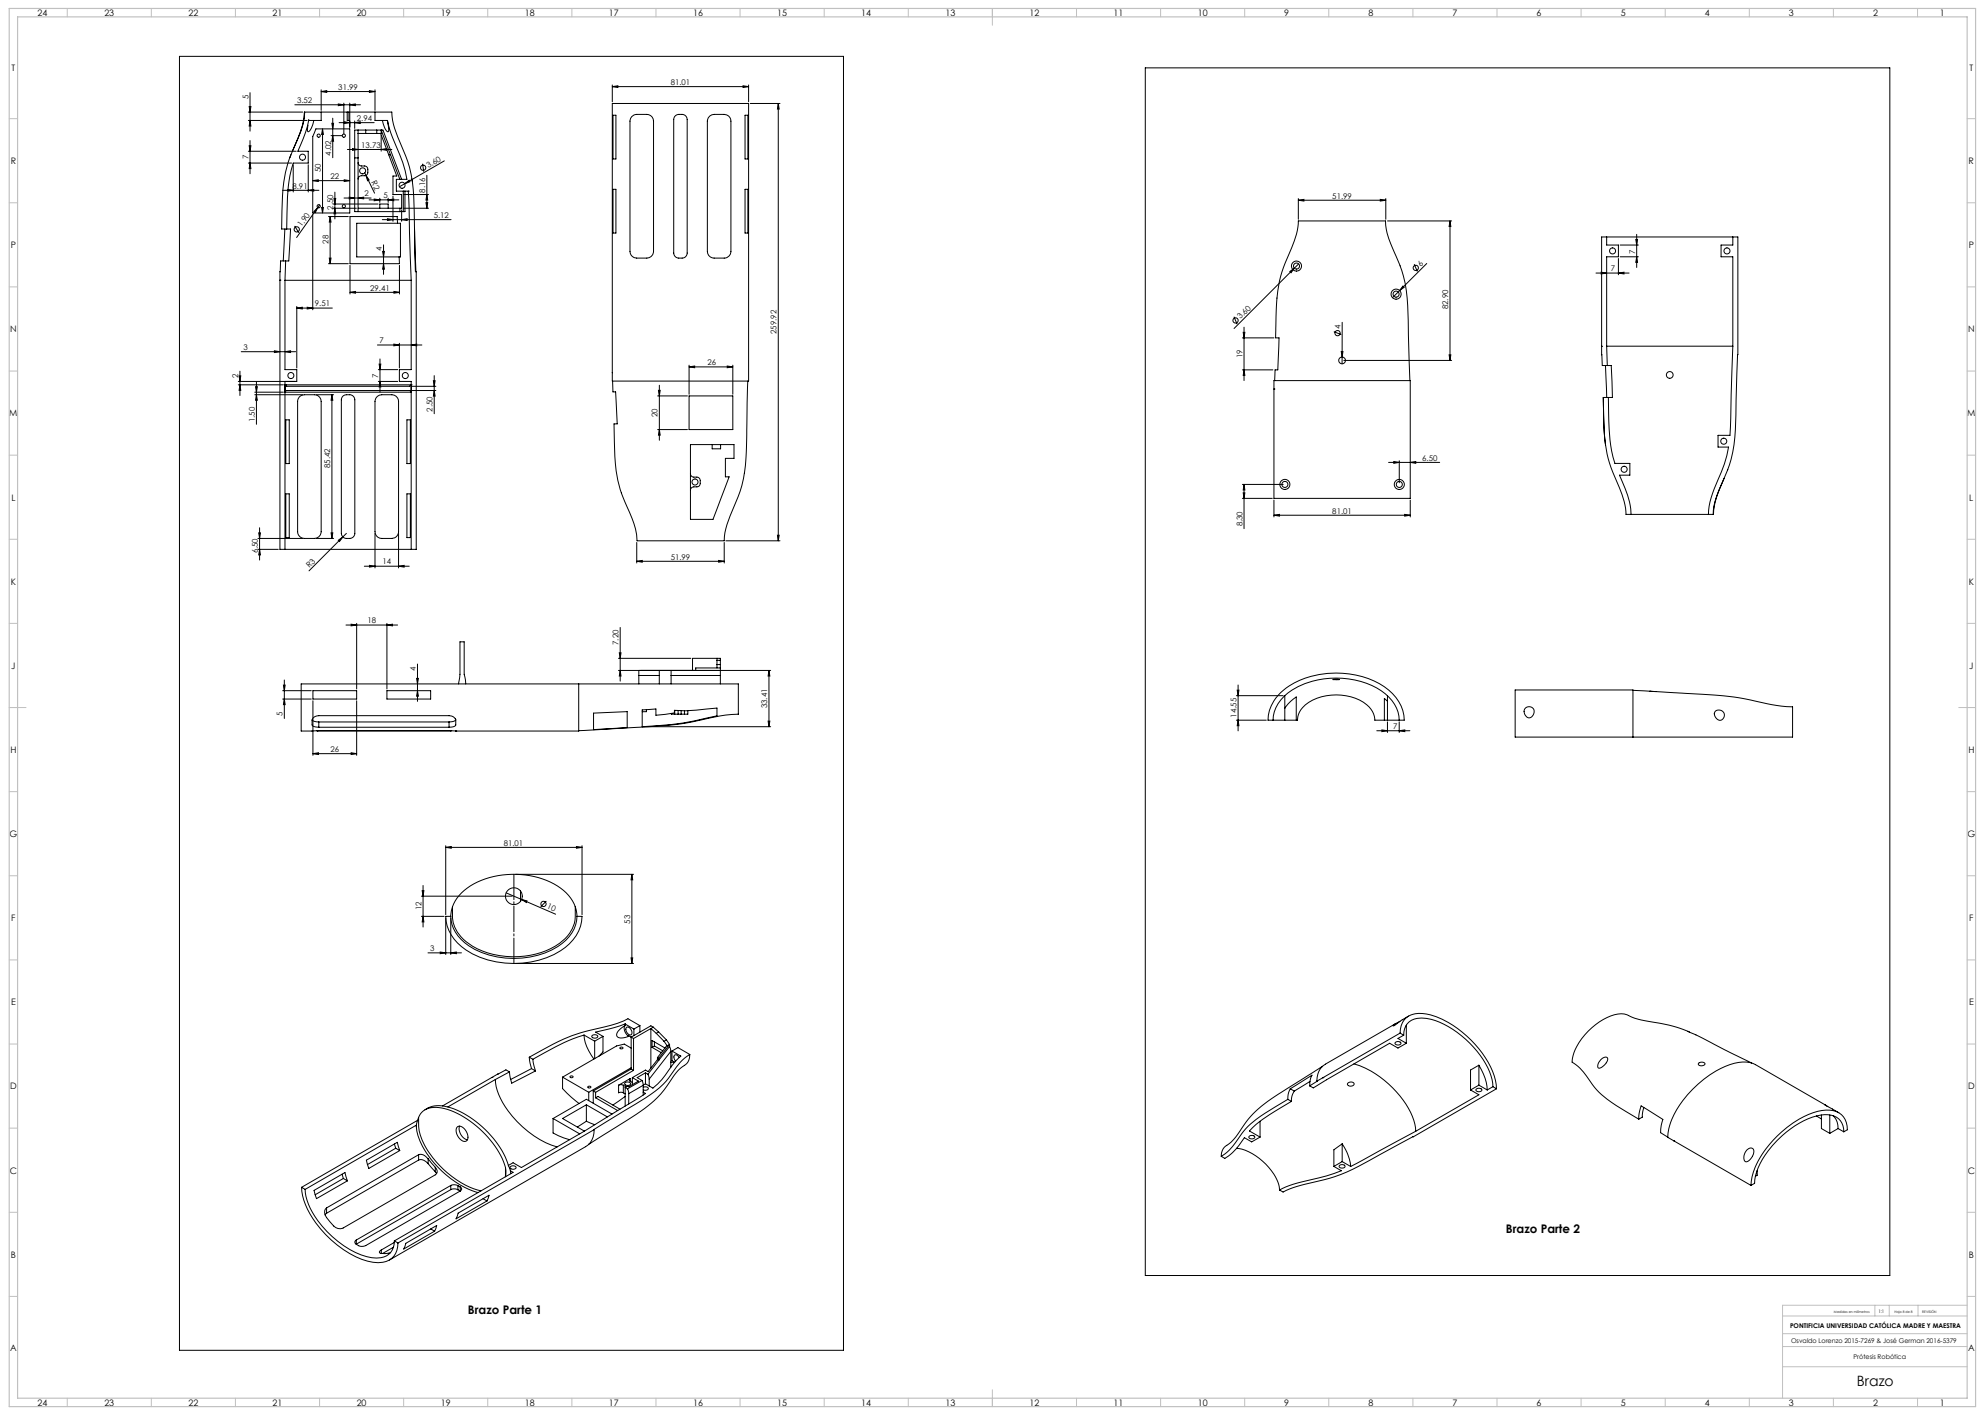
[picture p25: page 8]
Brazo Parte 1; Brazo Parte 2; Hoja 8 de 8; REVISIÓN

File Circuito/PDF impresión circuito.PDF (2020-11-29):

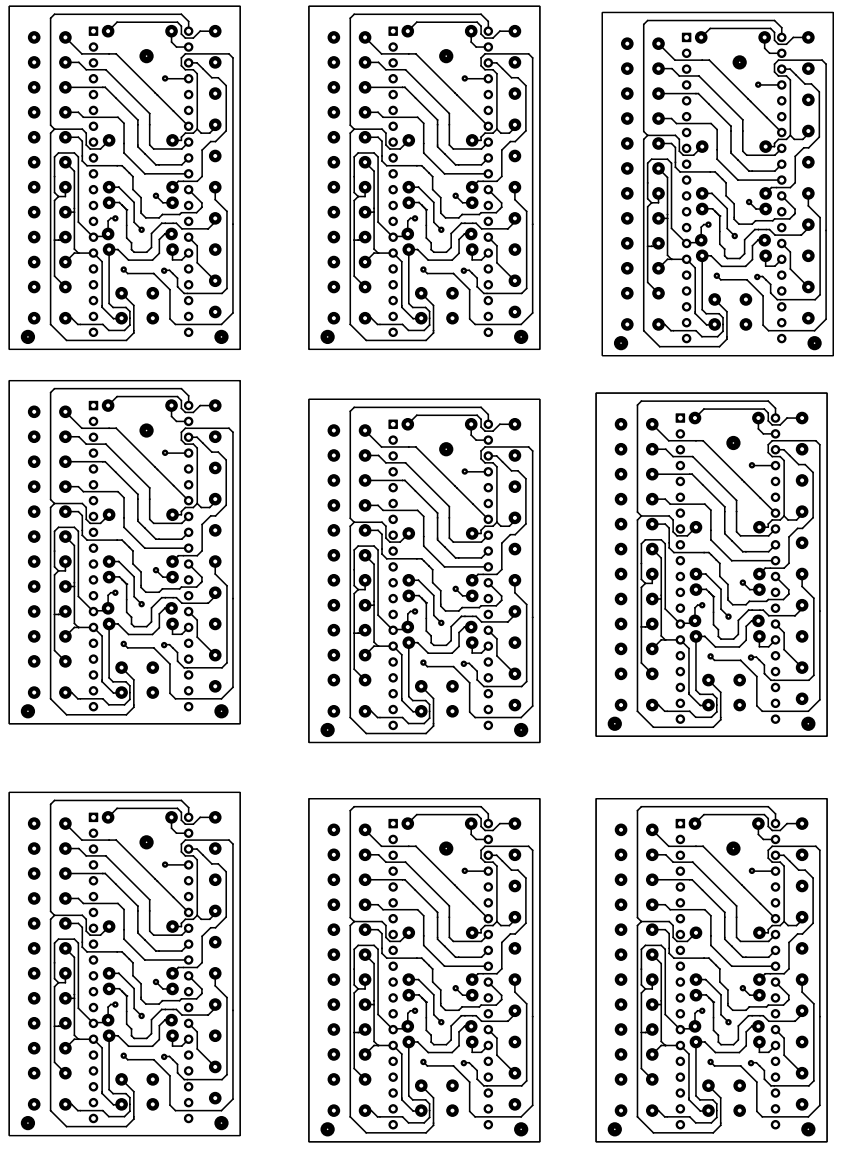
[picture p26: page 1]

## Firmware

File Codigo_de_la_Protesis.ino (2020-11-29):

#include <Servo.h>
#define R 3
#define G 5
#define B 6

Servo indice;
Servo mayor;
Servo anular;
Servo menique;
Servo pulgar;

unsigned long Tiempoentrada = 0;
int sensorValue = 0;
int p1_0s_0_5s = 0;
int p1_0_5s_1s  = 0;
int p1_1s_2s = 0;
int p1_2s_3s = 0;

int p2r2_0s_1s = 0;
int p2r2_1s_2s = 0;
int p2r2_2s_3s = 0;

int p2r3_0s_1s = 0;
int p2r3_1s_2s = 0;
int p2r3_2s_3s = 0;

int Sindice  = 180;;
int Smayor   = 180;;
int Sanular  = 180;;
int Smenique = 180;
int Spulgar  = 70;;

int Mindice  = 0;
int Mmayor   = 0;
int Manular  = 0;
int Mmenique = 0;
int Mpulgar  = 0;



void setup() {
  // initialize serial communication at 9600 bits per second:
  Serial.begin(9600);
  pinMode(8,INPUT);
  pinMode(R,OUTPUT);
  pinMode(G,OUTPUT);
  pinMode(B,OUTPUT);

  indice.attach(5);  
  mayor.attach(4);
  anular.attach(3);
  menique.attach(2);
  pulgar.attach(6);
  
  indice.write(180);
  mayor.write(180);
  anular.write(180);
  menique.write(180);

}

// the loop routine runs over and over again forever:
void loop() {
  /*--------------------------------------------------------LOOP------------------------------------------------------*/


  sensorValue = digitalRead(8);
  
  if (sensorValue  == 1){ 
    Tiempoentrada=millis();
    
    while (sensorValue  == 1){
      sensorValue = digitalRead(8);
      Serial.println(sensorValue);
      
      if ((millis() - Tiempoentrada) < 500 ){
        p1_0s_0_5s = 1;
        p1_0_5s_1s = 0;
        p1_1s_2s   = 0;
        p1_2s_3s   = 0;
      }
      
      if ((millis() - Tiempoentrada) > 500 and (millis() - Tiempoentrada) < 1000){
        analogWrite(R,255);
        analogWrite(G,0);
        analogWrite(B,0);
        p1_0s_0_5s = 0;
        p1_0_5s_1s = 1;
        p1_1s_2s   = 0;
        p1_2s_3s   = 0;
      }
      
      if ((millis() - Tiempoentrada) >1000 and (millis() - Tiempoentrada) < 2000){
        analogWrite(R,0);
        analogWrite(G,255);
        analogWrite(B,0);
        p1_0s_0_5s = 0;
        p1_0_5s_1s = 0;
        p1_1s_2s   = 1;
        p1_2s_3s   = 0;
      }
      
      if ((millis() - Tiempoentrada) > 2000){
        analogWrite(R,0);
        analogWrite(G,0);
        analogWrite(B,255);
        p1_0s_0_5s = 0;
        p1_0_5s_1s = 0;
        p1_1s_2s   = 0;
        p1_2s_3s   = 1;
      }
    }
    if(p1_0_5s_1s == 1){
      abrir();
    }
    if (p1_0s_0_5s == 1){
       cerrar();
    }
}




  while(p1_1s_2s == 1){
   sensorValue = digitalRead(8);
  
   if (sensorValue == 1){ 
    Tiempoentrada=millis();
    
    while (sensorValue == 1){
      sensorValue = digitalRead(8);
      Serial.println(sensorValue);
      
      if ((millis() - Tiempoentrada) < 1000){
        analogWrite(R,255);
        analogWrite(G,255);
        analogWrite(B,255);
        p2r2_0s_1s = 1;
        p2r2_1s_2s = 0;
        p2r2_2s_3s = 0;
      }
      
      if ((millis() - Tiempoentrada) >1000 and (millis() - Tiempoentrada) < 2000){
        analogWrite(R,255);
        analogWrite(G,255);
        analogWrite(B,0);
        p2r2_0s_1s = 0;
        p2r2_1s_2s = 1;
        p2r2_2s_3s = 0 ;
      }
      
      if ((millis() - Tiempoentrada) > 2000){
        analogWrite(R,255);
        analogWrite(G,0);
        analogWrite(B,255);
        p2r2_0s_1s = 0;
        p2r2_1s_2s = 0;
        p2r2_2s_3s = 1;
      }
    }
    if(p2r2_0s_1s == 1){
      cilindrico();
      p2r2_0s_1s = 0;
    }
    if(p2r2_1s_2s == 1){
      gancho();
      p2r2_1s_2s = 0;
    }
    if(p2r2_2s_3s == 1) {
      punta();
      p2r2_2s_3s = 0; 
      }
    p1_1s_2s = 0;
}  
  }




  while(p1_2s_3s == 1){
  sensorValue = digitalRead(8);
  
  if (sensorValue == 1){ 
    Tiempoentrada=millis();
    
    while (sensorValue ==1){
      sensorValue = digitalRead(8);
      Serial.println(sensorValue);
      
      if ((millis() - Tiempoentrada) < 1000){
        analogWrite(R,255);
        analogWrite(G,255);
        analogWrite(B,255);
        p2r3_0s_1s = 1;
        p2r3_1s_2s = 0;
        p2r3_2s_3s = 0;
      }
      
      if ((millis() - Tiempoentrada) > 1000 and (millis() - Tiempoentrada) < 2000){
        analogWrite(R,255);
        analogWrite(G,255);
        analogWrite(B,0);
        p2r3_0s_1s = 0;
        p2r3_1s_2s = 1;
        p2r3_2s_3s = 0 ;
      }
      
      if ((millis() - Tiempoentrada) > 2000){
        analogWrite(R,255);
        analogWrite(G,0);
        analogWrite(B,255);
        p2r3_0s_1s = 0;
        p2r3_1s_2s = 0;
        p2r3_2s_3s = 1;
      }
    }
    if(p2r3_0s_1s == 1){
      cerrarpulgar();
      p2r3_0s_1s = 0;
    }
    if(p2r3_1s_2s == 1){
      senalar();
      p2r3_1s_2s = 0;
    }
    if(p2r3_2s_3s == 1) {
      tresdedos();
      p2r3_2s_3s = 0;
      }
    p1_2s_3s = 0;
}  
  }



  analogWrite(R,0);
  analogWrite(G,0);
  analogWrite(B,0);
}


/*------------------------------------FUNCIONES-------------------------------------*/
void mover(){
  pulgar.write (Spulgar);
  indice.write (Sindice);
  mayor.write  (Smayor);
  anular.write (Sanular);
  menique.write(Smenique);
}

void cerrar(){
  Serial.println("cerrar");
  if (Mpulgar  == 1){Spulgar  += 7;}
  if (Mindice  == 1){if(Sindice > 20){Sindice  -= 10;}}
  if (Mmayor   == 1){Smayor   -= 10;}
  if (Manular  == 1){Sanular  -= 10;}
  if (Mmenique == 1){Smenique -= 10;}

  mover();
}

void abrir(){
  Serial.println("abrir");
  Spulgar  = 40;  
  Sindice  = 180;
  Smayor   = 180;
  Sanular  = 180;
  Smenique = 180;

  Mpulgar  = 0;
  Mindice  = 0;
  Mmayor   = 0;
  Manular  = 0;
  Mmenique = 0; 


  mover();
}
//---------------------- P1/1s<t<2s
void cilindrico(){
  Serial.println("cilindrico"); 
  
  Spulgar  = 80;
  Sindice  = 80;
  Smayor   = 80;
  Sanular  = 80;
  Smenique = 100;

  Mpulgar  = 1; 
  Mindice  = 1;
  Mmayor   = 1;
  Manular  = 1;
  Mmenique = 1;


  mover();
}

void gancho(){
  Serial.println("gancho"); 
  Sindice  = 80;
  Smayor   = 80;
  Sanular  = 80;
  Smenique = 100;
  
  Mpulgar  = 0;  
  Mindice  = 1;
  Mmayor   = 1;
  Manular  = 1;
  Mmenique = 1;
  
  mover();

}

void punta(){
  Serial.println("punta");
  
  Spulgar  = 80;
  Sindice  = 50;
  Smayor   = 180;
  Sanular  = 180;
  Smenique = 180;

  Mpulgar  = 1; 
  Mindice  = 1;
  Mmayor   = 0;
  Manular  = 0;
  Mmenique = 0;
 

  mover();
}


//---------------------- P1/2s<t<3s
void cerrarpulgar(){
  Spulgar  = 80;
  Sindice  = 180;
  Smayor   = 180;
  Sanular  = 180;
  Smenique = 180;

  Mpulgar  = 1;  
  Mindice  = 0;
  Mmayor   = 0;
  Manular  = 0;
  Mmenique = 0;

  
  mover();
}

void senalar(){
  Serial.println("senalar"); 
  Spulgar  = 115;
  Sindice  = 180;
  Smayor   = 0;
  Sanular  = 0;
  Smenique = 0;

  Mpulgar  = 0; 
  Mindice  = 0;
  Mmayor   = 0;
  Manular  = 0;
  Mmenique = 0;
 
  
  mover();
}

void tresdedos(){
  Serial.println("tresdedos");   
  Spulgar  = 80;
  Sindice  = 50;
  Smayor   = 50;
  Sanular  = 0;
  Smenique = 0;

  Mpulgar  = 1;  
  Mindice  = 1;
  Mmayor   = 1;
  Manular  = 0;
  Mmenique = 0;


  mover();
}
